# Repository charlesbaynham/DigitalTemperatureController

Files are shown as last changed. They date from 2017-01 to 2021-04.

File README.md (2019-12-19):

Digital Temperature Controller
==============================

_Copyright Charles Baynham 2018_

This repository holds a design for a digital temperature controller. The controller is designed for taking high precision
temperature measurements via a thermistor and applying low bandwidth PID feedback in response. 

This README file gives a brief overview of the device, but a much more detailed description is available in the manual, located in 
`./Manual`. 

`./Board design` contains schematics and PCB layouts for the controller board. This was produced in the open-source software KiCad. 

`./Code_for_microcontroller` contains the C++ code that must run on the on-board microcontroller. 

`./Code for Labview` contains a sample LabView application for controlling the device. See warning below...

Output
------

Output is by OPA458 high power opamps. Output can be up to 1A continuous, at voltages up to ±15V depending on the power supply.

Input
-----

Error signal acquisition is done by taking a balanced measurement between a thermistor
and a set resistor. The board produces an excitation voltage and measures
the difference in current between the thermistor and resistor to produce a temperature
measurement. For less demanding applications the set resistor can be on-board. For the
highest stability, the precision resistor should be placed next to its paired thermistor.
This measurement is performed by an INA330 chip, of which there are two present on
the board. The entire analogue section is electrically isolated from the rest of the board to
prevent noise on the electrical ground affecting the measurement.

Control
-------

The board can be controlled using a (virtual) serial connection over either USB or RS-485. Both of these interfaces 
are galvanically isolated to prevent electrical interference. The on-board microcontroller permits headless operation of the
device, and commands may be issued using a LabView interface.

Code
----

The code running on the device is written in c++ and has been well tested. The LabView control interface, designed to be run on a monitoring computer, is less well-tested and should be used at your own peril! For integration into an experimental system, control the device by issuing serial commands detail in the supplied manual. 

Manual
------

You should go read it now. It's in `./Manual`. 

Extensions
----------

The board is designed to break out the important analog (and come digital) connections, so that additional functionality can be enabled by adding a daughter-board to the main board. For example, you might 
* Require higher output currents
* Not need current driving capability, but would prefer very low-noise output instead
* Need an extreme level of stability, so use an external, ovenized voltage reference

None of these daughter-boards yet exist, but the interface required to create them exists from V5 onwards. 

Initial setup
-------------

The microcontroller needs to be flashed using Atmel Studio and an ISP programmer. You should either:

1. Set the fuses as described in `fuse_settings.txt`
2. Flash the bootloader saved as `optiboot_atmega328_custom_NANO.hex`
3. Use the Arduino IDE to compile and upload the latest version of the code

OR

1. Flash the complete production `.elf` file stored in `.\Code_for_microcontroller` using Atmel Studio, making sure to select "Flash", "Fuses" and "Verify Device ID" in Atmel Studio. This will give you whatever version of the code was stored in this `.elf` file, you can then update it using the Arduino IDE if you want to make changes.

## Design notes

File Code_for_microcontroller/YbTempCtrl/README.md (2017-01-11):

Yb+ temperature controller
==========================

Introduction  							{#sec-intro}
============

This is the source code for the Yb+ temperature controller, programmed and designed by <a href="mailto:charles.baynham@npl.co.uk">Charles Baynham</a>.

It is intended for high precision control of cavities, however can be used to control laser diode temperature or other low-bandwidth lock processes that could benefit from digital control. Error signal input can be either by voltage (from -5V to +5V) or through a balanced thermistor reading, mediated by a built-in INA330 IC. For demanding temperature applications, the latter method is recommended.

This code is designed to be uploaded to an ATMega328 microprocessor. It is written in C++ and can be compiled and uploaded via the Arduino IDE. However, if you intend to work on it for any significant length of time, I _highly_ recommend that you install a more capable IDE. I wrote this software in Visual Studio Community which is a free download from Microsoft and will make your life so much easier. 

Documentation 							{#sec-docs}
=============

If you are reading these comments in a pdf or html format then you are currently looking at the compiled documentation. If, however, you are reading this README.md file in a text editor then your first step before editing the code should be to get hold of the full code documentation. 

The code is documented throughout using the Doxygen commenting system. These can be compiled easily into a pdf or a local html website by:

1. Installing Doxygen from http://www.stack.nl/~dimitri/doxygen/download.html
2. Using the Doxygen GUI to load the file in this folder, `Doxyfile`
3. Selecting `Run doxygen` on the `Run` tab. 

This will produce the html documentation and, if you have pdflatex installed, source files for a pdf. 

Alternativly, open the Documentation.pdf file that should be bundled with this repo.  

Version Control 						{#sec-vc}
===============

This folder is a GIT repository that maintains a full history of development including every change since this code was started. This history is contained in a hidden folder called `.git` which should not be accessed directly. 

The upshot of this is that the code you see may not be the latest, and may instead be a "snapshot" of a previous state. To ensure you are looking at the latest iteration, and to make updates, install a git client of your choosing. https://windows.github.com/ is very lightweight, http://www.sourcetreeapp.com/ is more fully featured and https://desktop.github.com/ strikes a balance between the two.  

Once installed, "checkout" the master branch for the latest code version. See http://rogerdudler.github.io/git-guide/ for a simple guide. 

Note that this code makes use of several submodules. If you "clone" the code, you will by default not get these. In order to correctly get the code for these as well, run the command `git submodule update --init --recursive` after cloning the main code. If you use a more advanced GUI such as SourceTree then this should be handled for you automatically. 

Available commands						{#sec-commands}
=============

The device listens for commands on a virtual serial COM port served via USB. The USB connection is electrically isolated to avoid ground pollution. 

__Baud rate should be set to 57600.__

The board also contains footprints to enable RS485 communication via a backplane connection, however this is not yet implemented. 

For a detailed description of all the commands available, see the documentation for CommandDefinitions.h.

Code outline							{#sec-codeoutline}
=============

This code is split into classes according to the object orientated paradigm. A typical lock could be implemented as follows:

1. Define a YbCtrl::ErrorChannel object (or rather, an implementation of YbCtrl::ErrorChannel) to handle input.
2. Define a YbCtrl::CtrlChannel object to handle output
3. Define a YbCtrl::Algorithm object to implement the locking transfer function required.
4. Pass these three objects to a new YbCtrl::Controller object.
5. Loop, calling YbCtrl::Controller::doLoop() on each iteration. 

For more detail, every class and method is individually documented. See the Classes section or the Namespaces section to see more. 

@todo Implement RS485 Modbus protocol

@copyright Charles Baynham 2016

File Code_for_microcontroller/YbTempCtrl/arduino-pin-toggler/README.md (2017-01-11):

arduino-pin-toggler
===================

Introduction						{#sec-Introduction}
=============

This Arduino library manages the toggling of arbitary pins at controllable rates.
For example, it can be used to flash an LED at different speeds according
to the state of your device.

It works using interrupts and is designed to be lightweight when running,
so will not interfere with existing code.

This library requires exclusive usage of TIMER1 so is incompatible with
libraries that also use this timer.

Usage						{#sec-Usage}
=============

Include the class by adding `#include <pinToggler.h>` to your sketch.

Init the class by passing it an array of pins that will be toggled. E.g.

	int pins[3] = {13, A4, A5};
	pinToggler<3>::init(pins);

The template parameter (`<3>` above) defines the total number of pins being controlled.

These pins will start `LOW`, not toggling.

To start the toggling, set their speed to `OFF`, `SLOW`, `MEDIUM`, `FAST` or `MAX`. E.g.

	pinToggler<3>::setFlashRate(0, SLOW);

N.B. The template parameter (here `<3>`) must match the one used in pinToggler::init() or this will
throw an error. Also the LED parameter in pinToggler::setFlashRate refers to the pins passed to pinToggler::init(), zero-indexed
in the order that they appeared in in the array.

The speeds refer to fractions of the max speed, defined by #FLASH_FREQ_HZ.

@warning Note that all the function calls here are static members of the
class. Although a class object is created, this happens internally. For memory
management purposes, be aware that this class allocates `3 * numPins` bytes on
the heap. Thus, to avoid memory framentation, pinToggler::init() should be
called as early in your code as possible.

@copyright Charles Baynham 2016

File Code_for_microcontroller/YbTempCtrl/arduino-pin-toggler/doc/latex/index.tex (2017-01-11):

\hypertarget{index_Introduction}{}\section{Introduction}\label{index_Introduction}
This Arduino library manages the toggling of arbitary pins at controllable rates. For example, it can be used to flash an L\+ED at different speeds according to the state of your device.

It works using interrupts and is designed to be lightweight when running, so will not interfere with existing code.

This library requires exclusive usage of T\+I\+M\+E\+R1 so is incompatible with libraries that also use this timer.\hypertarget{index_Usage}{}\section{Usage}\label{index_Usage}
Include the class by adding {\ttfamily \#include $<$\hyperlink{pin_toggler_8h}{pin\+Toggler.\+h}$>$} to your sketch.

Init the class by passing it an array of pins that will be toggled. E.\+g. \begin{DoxyVerb}int pins[3] = {13, A4, A5};
pinToggler<3>::init(pins);
\end{DoxyVerb}

The template parameter ({\ttfamily $<$3$>$} above) defines the total number of pins being controlled.

These pins will start {\ttfamily L\+OW}, not toggling.

To start the toggling, set their speed to {\ttfamily O\+FF}, {\ttfamily S\+L\+OW}, {\ttfamily M\+E\+D\+I\+UM}, {\ttfamily F\+A\+ST} or {\ttfamily M\+AX}. E.\+g. \begin{DoxyVerb}pinToggler<3>::setFlashRate(0, SLOW);
\end{DoxyVerb}

N.\+B. The template parameter (here {\ttfamily $<$3$>$}) must match the one used in \hyperlink{classpin_toggler_aa58211817601d0e2dd413eb63e41f773}{pin\+Toggler\+::init()} or this will throw an error. Also the L\+ED parameter in \hyperlink{classpin_toggler_a42ae0ac4f841dae592195f26bffb109e}{pin\+Toggler\+::set\+Flash\+Rate} refers to the pins passed to \hyperlink{classpin_toggler_aa58211817601d0e2dd413eb63e41f773}{pin\+Toggler\+::init()}, zero-\/indexed in the order that they appeared in in the array.

The speeds refer to fractions of the max speed, defined by \hyperlink{pin_toggler_8h_a1097b75ec2a0f9ad2e6d4f6c4500d224}{F\+L\+A\+S\+H\+\_\+\+F\+R\+E\+Q\+\_\+\+HZ}.

\begin{DoxyWarning}{Warning}
Note that all the function calls here are static members of the class. Although a class object is created, this happens internally. For memory management purposes, be aware that this class allocates {\ttfamily 3 $\ast$ num\+Pins} bytes on the heap. Thus, to avoid memory framentation, \hyperlink{classpin_toggler_aa58211817601d0e2dd413eb63e41f773}{pin\+Toggler\+::init()} should be called as early in your code as possible.
\end{DoxyWarning}
\begin{DoxyCopyright}{Copyright}
Charles Baynham 2016 
\end{DoxyCopyright}

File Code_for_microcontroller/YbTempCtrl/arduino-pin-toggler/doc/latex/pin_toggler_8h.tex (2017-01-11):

\hypertarget{pin_toggler_8h}{}\section{pin\+Toggler.\+h File Reference}
\label{pin_toggler_8h}\index{pin\+Toggler.\+h@{pin\+Toggler.\+h}}

Contains all the code for the arduino-\/pin-\/toggler library.  

\subsection*{Classes}
\begin{DoxyCompactItemize}
\item 
class \hyperlink{classpin_toggler}{pin\+Toggler$<$ num\+Pins $>$}
\begin{DoxyCompactList}\small\item\em Class for toggling pins. \end{DoxyCompactList}\end{DoxyCompactItemize}
\subsection*{Macros}
\begin{DoxyCompactItemize}
\item 
\#define \hyperlink{pin_toggler_8h_a0fac869d83ac1a584d6c45cf609f5fe7}{P\+R\+E\+S\+C\+A\+L\+ER}~1024
\begin{DoxyCompactList}\small\item\em The prescaler for T\+I\+M\+E\+R1. \end{DoxyCompactList}\item 
\#define \hyperlink{pin_toggler_8h_a1097b75ec2a0f9ad2e6d4f6c4500d224}{F\+L\+A\+S\+H\+\_\+\+F\+R\+E\+Q\+\_\+\+HZ}~8
\begin{DoxyCompactList}\small\item\em How often the I\+SR will trigger. \end{DoxyCompactList}\end{DoxyCompactItemize}
\subsection*{Enumerations}

\subsection{Detailed Description}
Contains all the code for the arduino-\/pin-\/toggler library. 

\subsection{Macro Definition Documentation}
\index{pin\+Toggler.\+h@{pin\+Toggler.\+h}!F\+L\+A\+S\+H\+\_\+\+F\+R\+E\+Q\+\_\+\+HZ@{F\+L\+A\+S\+H\+\_\+\+F\+R\+E\+Q\+\_\+\+HZ}}
\index{F\+L\+A\+S\+H\+\_\+\+F\+R\+E\+Q\+\_\+\+HZ@{F\+L\+A\+S\+H\+\_\+\+F\+R\+E\+Q\+\_\+\+HZ}!pin\+Toggler.\+h@{pin\+Toggler.\+h}}
\subsubsection[{\texorpdfstring{F\+L\+A\+S\+H\+\_\+\+F\+R\+E\+Q\+\_\+\+HZ}{FLASH_FREQ_HZ}}]{\setlength{\rightskip}{0pt plus 5cm}\#define F\+L\+A\+S\+H\+\_\+\+F\+R\+E\+Q\+\_\+\+HZ~8}\hypertarget{pin_toggler_8h_a1097b75ec2a0f9ad2e6d4f6c4500d224}{}\label{pin_toggler_8h_a1097b75ec2a0f9ad2e6d4f6c4500d224}

How often the I\+SR will trigger. 

This defines the max toggle rate. In combination with the \hyperlink{pin_toggler_8h_a8f10e927d4361fa9c8ecfc7a0b163943}{F\+L\+A\+S\+H\+R\+A\+TE} chosen with \hyperlink{classpin_toggler_a42ae0ac4f841dae592195f26bffb109e}{pin\+Toggler\+::set\+Flash\+Rate}, this determines the rate at which the pins will toggle. \index{pin\+Toggler.\+h@{pin\+Toggler.\+h}!P\+R\+E\+S\+C\+A\+L\+ER@{P\+R\+E\+S\+C\+A\+L\+ER}}
\index{P\+R\+E\+S\+C\+A\+L\+ER@{P\+R\+E\+S\+C\+A\+L\+ER}!pin\+Toggler.\+h@{pin\+Toggler.\+h}}
\subsubsection[{\texorpdfstring{P\+R\+E\+S\+C\+A\+L\+ER}{PRESCALER}}]{\setlength{\rightskip}{0pt plus 5cm}\#define P\+R\+E\+S\+C\+A\+L\+ER~1024}\hypertarget{pin_toggler_8h_a0fac869d83ac1a584d6c45cf609f5fe7}{}\label{pin_toggler_8h_a0fac869d83ac1a584d6c45cf609f5fe7}

The prescaler for T\+I\+M\+E\+R1. 

This value is used to calculate the correct value to start T\+I\+M\+E\+R1 on, given this prescaler factor.

This does not need to be changed unless you need particularly fast flash rates.

Specifically, if your application requires {\ttfamily 16000000 / P\+R\+E\+S\+C\+A\+L\+ER / F\+L\+A\+S\+H\+\_\+\+F\+R\+E\+Q\+\_\+\+HZ $>$= 65536} you will need to alter the prescaler value both here and where it is set in the private setup\+Singleton() method. 

\subsection{Enumeration Type Documentation}
\index{pin\+Toggler.\+h@{pin\+Toggler.\+h}!F\+L\+A\+S\+H\+R\+A\+TE@{F\+L\+A\+S\+H\+R\+A\+TE}}
\index{F\+L\+A\+S\+H\+R\+A\+TE@{F\+L\+A\+S\+H\+R\+A\+TE}!pin\+Toggler.\+h@{pin\+Toggler.\+h}}
\subsubsection[{\texorpdfstring{F\+L\+A\+S\+H\+R\+A\+TE}{FLASHRATE}}]{\setlength{\rightskip}{0pt plus 5cm}enum {\bf F\+L\+A\+S\+H\+R\+A\+TE}}\hypertarget{pin_toggler_8h_a8f10e927d4361fa9c8ecfc7a0b163943}{}\label{pin_toggler_8h_a8f10e927d4361fa9c8ecfc7a0b163943}

Flash rate options. 

These rates are used as parameters to the set\+Flash\+Rate method.

In combination with F\+L\+A\+S\+H\+\_\+\+F\+R\+E\+Q\+\_\+\+HZ, these set the flash rate of an L\+ED.

O\+FF and ON allow you to disable flashing, leaving the L\+ED either on or off. \begin{Desc}
\item[Enumerator]\par
\begin{description}
\index{ON@{ON}!pin\+Toggler.\+h@{pin\+Toggler.\+h}}\index{pin\+Toggler.\+h@{pin\+Toggler.\+h}!ON@{ON}}\item[{\em 
ON\hypertarget{pin_toggler_8h_a8f10e927d4361fa9c8ecfc7a0b163943a977d478dacaae531f95695750d1e9d03}{}\label{pin_toggler_8h_a8f10e927d4361fa9c8ecfc7a0b163943a977d478dacaae531f95695750d1e9d03}
}]Always on \index{O\+FF@{O\+FF}!pin\+Toggler.\+h@{pin\+Toggler.\+h}}\index{pin\+Toggler.\+h@{pin\+Toggler.\+h}!O\+FF@{O\+FF}}\item[{\em 
O\+FF\hypertarget{pin_toggler_8h_a8f10e927d4361fa9c8ecfc7a0b163943aac132f2982b98bcaa3445e535a03ff75}{}\label{pin_toggler_8h_a8f10e927d4361fa9c8ecfc7a0b163943aac132f2982b98bcaa3445e535a03ff75}
}]Always off \index{S\+L\+OW@{S\+L\+OW}!pin\+Toggler.\+h@{pin\+Toggler.\+h}}\index{pin\+Toggler.\+h@{pin\+Toggler.\+h}!S\+L\+OW@{S\+L\+OW}}\item[{\em 
S\+L\+OW\hypertarget{pin_toggler_8h_a8f10e927d4361fa9c8ecfc7a0b163943ab27edad9d3e126dc8448b6030438adb6}{}\label{pin_toggler_8h_a8f10e927d4361fa9c8ecfc7a0b163943ab27edad9d3e126dc8448b6030438adb6}
}]Flash at F\+L\+A\+S\+H\+\_\+\+F\+R\+E\+Q\+\_\+\+HZ / 8 \index{M\+E\+D\+I\+UM@{M\+E\+D\+I\+UM}!pin\+Toggler.\+h@{pin\+Toggler.\+h}}\index{pin\+Toggler.\+h@{pin\+Toggler.\+h}!M\+E\+D\+I\+UM@{M\+E\+D\+I\+UM}}\item[{\em 
M\+E\+D\+I\+UM\hypertarget{pin_toggler_8h_a8f10e927d4361fa9c8ecfc7a0b163943a5340ec7ecef6cc3886684a3bd3450d64}{}\label{pin_toggler_8h_a8f10e927d4361fa9c8ecfc7a0b163943a5340ec7ecef6cc3886684a3bd3450d64}
}]Flash at F\+L\+A\+S\+H\+\_\+\+F\+R\+E\+Q\+\_\+\+HZ / 2 \index{F\+A\+ST@{F\+A\+ST}!pin\+Toggler.\+h@{pin\+Toggler.\+h}}\index{pin\+Toggler.\+h@{pin\+Toggler.\+h}!F\+A\+ST@{F\+A\+ST}}\item[{\em 
F\+A\+ST\hypertarget{pin_toggler_8h_a8f10e927d4361fa9c8ecfc7a0b163943af84c11ba888e499a8a282a3e6f5de7de}{}\label{pin_toggler_8h_a8f10e927d4361fa9c8ecfc7a0b163943af84c11ba888e499a8a282a3e6f5de7de}
}]Flash at F\+L\+A\+S\+H\+\_\+\+F\+R\+E\+Q\+\_\+\+HZ / 4 \index{M\+AX@{M\+AX}!pin\+Toggler.\+h@{pin\+Toggler.\+h}}\index{pin\+Toggler.\+h@{pin\+Toggler.\+h}!M\+AX@{M\+AX}}\item[{\em 
M\+AX\hypertarget{pin_toggler_8h_a8f10e927d4361fa9c8ecfc7a0b163943ad7e097bda6d981de2520f49fe74c25b7}{}\label{pin_toggler_8h_a8f10e927d4361fa9c8ecfc7a0b163943ad7e097bda6d981de2520f49fe74c25b7}
}]Flash at F\+L\+A\+S\+H\+\_\+\+F\+R\+E\+Q\+\_\+\+HZ \end{description}
\end{Desc}

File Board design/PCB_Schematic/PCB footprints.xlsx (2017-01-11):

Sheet: 1.25mm pitch, two rows
1 | $PAD^^nSh "1" R 1.5 1.5 0 0 0^^nDr 0.8 0 0^^nAt STD N 00E0FFFF^^nNe 1 ""^^nPo 0 0^^n$EndPAD | 2 | $PAD^^nSh "2" C 1.5 1.5 0 0 0^^nDr 0.8 0 0^^nAt STD N 00E0FFFF^^nNe 1 ""^^nPo 1.25 -5^^n$EndPAD
3 | $PAD^^nSh "3" C 1.5 1.5 0 0 0^^nDr 0.8 0 0^^nAt STD N 00E0FFFF^^nNe 1 ""^^nPo 2.5 0^^n$EndPAD | 4 | $PAD^^nSh "4" C 1.5 1.5 0 0 0^^nDr 0.8 0 0^^nAt STD N 00E0FFFF^^nNe 1 ""^^nPo 3.75 -5^^n$EndPAD
5 | $PAD^^nSh "5" C 1.5 1.5 0 0 0^^nDr 0.8 0 0^^nAt STD N 00E0FFFF^^nNe 1 ""^^nPo 5 0^^n$EndPAD | 6 | $PAD^^nSh "6" C 1.5 1.5 0 0 0^^nDr 0.8 0 0^^nAt STD N 00E0FFFF^^nNe 1 ""^^nPo 6.25 -5^^n$EndPAD
7 | $PAD^^nSh "7" C 1.5 1.5 0 0 0^^nDr 0.8 0 0^^nAt STD N 00E0FFFF^^nNe 1 ""^^nPo 7.5 0^^n$EndPAD | 8 | $PAD^^nSh "8" C 1.5 1.5 0 0 0^^nDr 0.8 0 0^^nAt STD N 00E0FFFF^^nNe 1 ""^^nPo 8.75 -5^^n$EndPAD
9 | $PAD^^nSh "9" C 1.5 1.5 0 0 0^^nDr 0.8 0 0^^nAt STD N 00E0FFFF^^nNe 1 ""^^nPo 10 0^^n$EndPAD | 10 | $PAD^^nSh "10" C 1.5 1.5 0 0 0^^nDr 0.8 0 0^^nAt STD N 00E0FFFF^^nNe 1 ""^^nPo 11.25 -5^^n$EndPAD
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

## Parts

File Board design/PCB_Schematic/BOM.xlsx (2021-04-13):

Ref | Value | Part | Footprint | Description | MPN | SPURL | MFR | SPR | SPN
C_filter1,C_filter2 | 1n | Device:C | Capacitor_SMD:C_0805_2012Metric_Pad1.15x1.40mm_HandSolder | Unpolarized capacitor | - | - | - | - | GENERIC
C1 | 22u | Device:C | Capacitors_ThroughHole:C_Radial_D5_L11_P2 | Unpolarized capacitor | - | - | - | - | GENERIC
C12,C13,C20,C21,C26,C27,C37,C38,C43,C45,C46,C47,C50,C52,C53,C54 | 100n | Device:CP | Capacitor_SMD:C_0805_2012Metric_Pad1.15x1.40mm_HandSolder | Polarized capacitor | - | - | - | - | GENERIC
C14,C15,C22,C23 | 100p | Device:C_Small | Capacitor_SMD:C_0805_2012Metric_Pad1.15x1.40mm_HandSolder | Unpolarized capacitor, small symbol | - | - | - | - | GENERIC
C2,C5 | 47u | Device:CP | Capacitors_ThroughHole:C_Radial_D5_L11_P2 | Polarized capacitor | - | - | - | - | GENERIC
C28 | 1u | Device:CP_Small | Capacitor_SMD:C_0805_2012Metric_Pad1.15x1.40mm_HandSolder | Polarized capacitor, small symbol | - | - | - | - | GENERIC
C29,C31,C34 | 100n | Device:CP_Small | Capacitor_SMD:C_0805_2012Metric_Pad1.15x1.40mm_HandSolder | Polarized capacitor, small symbol | - | - | - | - | GENERIC
C3,C4,C10,C11,C18,C19,C35,C36,C48,C55 | 1u | Device:CP | Capacitor_SMD:C_0805_2012Metric_Pad1.15x1.40mm_HandSolder | Polarized capacitor | - | - | - | - | GENERIC
C30,C32 | 8p | Device:C_Small | Capacitor_SMD:C_0805_2012Metric_Pad1.15x1.40mm_HandSolder | Unpolarized capacitor, small symbol | - | - | - | - | GENERIC
C33 | 100n | Device:C | Capacitor_SMD:C_0805_2012Metric_Pad1.15x1.40mm_HandSolder | Unpolarized capacitor | - | - | - | - | GENERIC
C39 | 4.7n | Device:C | Capacitor_SMD:C_0805_2012Metric_Pad1.15x1.40mm_HandSolder | Unpolarized capacitor | - | - | - | - | GENERIC
C40,C41 | 1u | Device:C | Capacitor_SMD:C_0805_2012Metric_Pad1.15x1.40mm_HandSolder | Unpolarized capacitor | - | - | - | - | GENERIC
C42,C44,C49,C51 | 15p | Device:C | Capacitor_SMD:C_0805_2012Metric_Pad1.15x1.40mm_HandSolder | Unpolarized capacitor | - | - | - | - | GENERIC
C57,C58 | 100n | Device:C_Small | Capacitor_SMD:C_0805_2012Metric_Pad1.15x1.40mm_HandSolder | Unpolarized capacitor, small symbol | - | - | - | - | GENERIC
C6,C7,C56 | 1u | Device:C_Small | Capacitor_SMD:C_0805_2012Metric_Pad1.15x1.40mm_HandSolder | Unpolarized capacitor, small symbol | - | - | - | - | GENERIC
C8,C9 | 10n | Device:C | Capacitor_SMD:C_0805_2012Metric_Pad1.15x1.40mm_HandSolder | Unpolarized capacitor | - | - | - | - | GENERIC
CON1 | BARREL_JACK | Connector:Barrel_Jack_Switch | Connector_BarrelJack:BarrelJack_Horizontal | DC Barrel Jack with an internal switch | 448-382 | - | RS Pro | RS | 448-382
D1 | Led_x2_split | Custom_Components:Led_x2_split | Custom:Double_LEDs |  | L-710A8MD/2ID | - | Kingbright | RS | 6164188
D2 | POWER | Device:LED | LEDs:LED_0805 | Light emitting diode | LG R971 | - | OSRAM | RS | 654-5773
D3 | TX | Device:LED | LEDs:LED_0805 | Light emitting diode | LG R971 | - | OSRAM | RS | 654-5773
D4 | RX | Device:LED | LEDs:LED_0805 | Light emitting diode | LG R971 | - | OSRAM | RS | 654-5773
D5 | SCLK | Device:LED | LEDs:LED_0805 | Light emitting diode | LG R971 | - | OSRAM | RS | 654-5773
D6 | LED | Device:LED | Custom:PCB_MOUNT_LED | Light emitting diode | L-93A8CB/1GD | - | Kingbright | RS | 466-4260
DB_ES1,DB_ES2,DB_OPA1,DB_OPA2 | PIN | Connector:Conn_01x01_Female | TestPoint:TestPoint_THTPad_1.5x1.5mm_Drill0.7mm | Generic connector, single row, 01x01, script generated (kicad-library-utils/schlib/autogen/connector/) | DNP | DNP | DNP | DNP | DNP
DB_GND1,DB_GND2,DB_GND3,DB_5V1,DB_VCC1,DB_VCC2,DB_VCC3 | PIN | Connector:Conn_01x01_Female | TestPoint:TestPoint_THTPad_3.0x3.0mm_Drill1.5mm | Generic connector, single row, 01x01, script generated (kicad-library-utils/schlib/autogen/connector/) | DNP | DNP | DNP | DNP | DNP
DISABLE_OPA1 | Disable_OPA1 | Jumper:Jumper_3_Bridged12 | Jumper:SolderJumper-3_P1.3mm_Bridged2Bar12_Pad1.0x1.5mm_NumberLabels | Jumper, 3-pole, pins 1+2 closed/bridged | DNP | DNP | DNP | DNP | DNP
DISABLE_OPA2 | Disable_OPA2 | Jumper:Jumper_3_Bridged12 | Jumper:SolderJumper-3_P1.3mm_Bridged2Bar12_Pad1.0x1.5mm_NumberLabels | Jumper, 3-pole, pins 1+2 closed/bridged | DNP | DNP | DNP | DNP | DNP
DISABLE_OPA3 | Disable_OPA3 | Jumper:Jumper_3_Bridged12 | Jumper:SolderJumper-3_P1.3mm_Bridged2Bar12_Pad1.0x1.5mm_NumberLabels | Jumper, 3-pole, pins 1+2 closed/bridged | DNP | DNP | DNP | DNP | DNP
DISABLE_OPA4 | Disable_OPA4 | Jumper:Jumper_3_Bridged12 | Jumper:SolderJumper-3_P1.3mm_Bridged2Bar12_Pad1.0x1.5mm_NumberLabels | Jumper, 3-pole, pins 1+2 closed/bridged | DNP | DNP | DNP | DNP | DNP
IC1 | ATMEGA328P-A | MCU_Microchip_ATmega:ATmega328P-AU | Housings_QFP:LQFP-32_7x7mm_Pitch0.8mm | 20MHz, 32kB Flash, 2kB SRAM, 1kB EEPROM, TQFP-32 | ATMEGA328P-A | - | Atmel | Farnell | 1715486
J1 | 5V_Outputs_1 | Connector_Generic:Conn_01x03 | Connector_PinHeader_2.54mm:PinHeader_1x03_P2.54mm_Vertical | Generic connector, single row, 01x03, script generated (kicad-library-utils/schlib/autogen/connector/) | - | - | - | - | GENERIC
J2 | External 2.5v ref | Connector:Conn_Coaxial | Connector_Coaxial:MMCX_Molex_73415-1471_Vertical | coaxial connector (BNC, SMA, SMB, SMC, Cinch/RCA, ...) | 73415-1471 | - | Molex | Digi-Key | WM5557-ND
J3 | 5V_Outputs_2 | Connector_Generic:Conn_01x03 | Connector_PinHeader_2.54mm:PinHeader_1x03_P2.54mm_Vertical | Generic connector, single row, 01x03, script generated (kicad-library-utils/schlib/autogen/connector/) | - | - | - | - | GENERIC
JP1 | DISABLE FLASH | Device:Jumper_NC_Dual | Pin_Headers:Pin_Header_Straight_1x03 | Dual jumper, normally closed | 09.03290.01 | - | EOZ | RS | 204-7865
JP2,JP3,JP4,JP5,JP6,JP7 | Jumper_NO_Small | Device:Jumper_NO_Small | Custom:SmallJumperNoCourtyard | Jumper, normally open, small symbol | DNP | DNP | DNP | DNP | DNP
P1 | 233-2977 | Connector_Generic:Conn_02x04_Odd_Even | Custom:Molex_Microfit3_Header_02x04_Angled_43045-080x_FIXED | Generic connector, double row, 02x04, odd/even pin numbering scheme (row 1 odd numbers, row 2 even numbers), script generated (kicad-library-utils/schlib/autogen/connector/) | 43045-0800 | - | Molex | RS | 233-2977
P2 | 820-8104 | Connector_Generic:Conn_01x08 | Custom:RJ45_TE | Generic connector, single row, 01x08, script generated (kicad-library-utils/schlib/autogen/connector/) | 1-406525-1 | - | TE Connectivity | RS | 820-8104
P3 | RS485 | Connector_Generic:Conn_01x04 | Connectors_Molex:Molex_PicoBlade_53048-0410_04x1.25mm_Angled | Generic connector, single row, 01x04, script generated (kicad-library-utils/schlib/autogen/connector/) | 53048-0410 | - | Molex | Digikey | WM1744-ND
P4 | USB_OTG | Connector:USB_OTG | Custom:MICRO-B_USB_TOP_MOUNT | USB mini/micro connector | 47590-0001 | - | MOLEX | Farnell | 1568022
P5 | ICSP | Connector_Generic:Conn_02x03_Odd_Even | Pin_Headers:Pin_Header_Straight_2x03 | Generic connector, double row, 02x03, odd/even pin numbering scheme (row 1 odd numbers, row 2 even numbers), script generated (kicad-library-utils/schlib/autogen/connector/) | 75869-131LF | - | Amphenol FCI | Digikey | 609-2845-ND
P6 | ADC breakout | Connector_Generic:Conn_02x04_Odd_Even | Pin_Headers:Pin_Header_Straight_2x04_Pitch1.27mm | Generic connector, double row, 02x04, odd/even pin numbering scheme (row 1 odd numbers, row 2 even numbers), script generated (kicad-library-utils/schlib/autogen/connector/) | DNP | DNP | DNP | DNP | DNP
R_gain1,R_gain2 | 22k_prec | Device:R | Resistor_SMD:R_0805_2012Metric_Pad1.15x1.40mm_HandSolder | Resistor | RG2012L-223-L-T05 | - | Susumu | Digikey | 408-1781-1-ND
R_Prec1,R_Prec2 | 10k_prec | Device:R | Custom:Resistor_Vertical_RM5mm_Cust | Resistor | Y0706-10KA-ND | - | Vishay | Digikey | Y0706-10KA-ND
R_Prec3 | 33k_prec | Device:R_Small | Resistor_SMD:R_0805_2012Metric_Pad1.15x1.40mm_HandSolder | Resistor, small symbol | RG2012L-333-L-T05 | - | Susumu | Digikey | 408-1781-1-ND
R_Prec4 | 22k_prec | Device:R_Small | Resistor_SMD:R_0805_2012Metric_Pad1.15x1.40mm_HandSolder | Resistor, small symbol | RG2012L-223-L-T05 | - | Susumu | Digikey | 408-1781-1-ND
R_R1,R_R2,R_T1,R_T2 | 1k_prec | Device:R_Small | Resistor_SMD:R_0805_2012Metric_Pad1.15x1.40mm_HandSolder | Resistor, small symbol | RG2012L-102-L-T05 | - | Susumu | Digikey | 408-1774-1-ND
R1,R2,R26,R29,R30,R31,R34,R37,R38,R39,R43 | 100R | Device:R | Resistor_SMD:R_0805_2012Metric_Pad1.15x1.40mm_HandSolder | Resistor | - | - | - | - | GENERIC
R10 | 1k | Device:R | Resistor_SMD:R_0805_2012Metric_Pad1.15x1.40mm_HandSolder | Resistor | - | - | - | - | GENERIC
R11,R40,R41,R42 | 10k | Device:R_Small | Resistor_SMD:R_0805_2012Metric_Pad1.15x1.40mm_HandSolder | Resistor, small symbol | - | - | - | - | GENERIC
R12,R14,R16,R18 | 51K | Device:R | Resistor_SMD:R_0805_2012Metric_Pad1.15x1.40mm_HandSolder | Resistor | - | - | - | - | GENERIC
R13,R15,R17,R19 | 200K | Device:R | Resistor_SMD:R_0805_2012Metric_Pad1.15x1.40mm_HandSolder | Resistor | - | - | - | - | GENERIC
R20,R_Ser1,R_Ser2 | 1k | Device:R_Small | Resistor_SMD:R_0805_2012Metric_Pad1.15x1.40mm_HandSolder | Resistor, small symbol | - | - | - | - | GENERIC
R3,R4,R5,R21,R22,R23 | 100R | Device:R_Small | Resistor_SMD:R_0805_2012Metric_Pad1.15x1.40mm_HandSolder | Resistor, small symbol | - | - | - | - | GENERIC
R8 | RS485_TERM | Device:R_Small | Resistor_THT:R_Axial_DIN0516_L15.5mm_D5.0mm_P5.08mm_Vertical | Resistor, small symbol | DNP | DNP | DNP | DNP | DNP
R9,R24,R25,R27,R28,R32,R33,R35,R36 | 10k | Device:R | Resistor_SMD:R_0805_2012Metric_Pad1.15x1.40mm_HandSolder | Resistor | - | - | - | - | GENERIC
SELECT_VRef1 | Select V_ref | Jumper:Jumper_3_Bridged12 | Jumper:SolderJumper-3_P1.3mm_Bridged2Bar12_Pad1.0x1.5mm_NumberLabels | Jumper, 3-pole, pins 1+2 closed/bridged | DNP | DNP | DNP | DNP | DNP
SW1 | DISABLE_COMMS | Switch:SW_SPDT | Custom:ApemSwitch | Switch, single pole double throw | TL36WW050 | - | APEM | RS | 664-288
U1 | LM7805 | Custom_Components:7805_mod | Custom:TO220_HORZ |  | LM7805CT/NOPB | - | Texas Instruments | Digikey | 296-47192-ND
U11 | ISO7242 | Custom_Components:ISO7242 | Housings_SOIC:SOIC-16_7.5x10.3mm_Pitch1.27mm |  | ISO7242 | - | TI | Mouser | 595-ISO7242CDW
U12 | FT232RL | Custom_Components:FT232RL | Housings_SSOP:SSOP-28_5.3x10.2mm_Pitch0.65mm |  | FT232RL | - | FTDI | Farnell | 1146032
U13 | ADS1262 | Custom_Components:ADS1262 | Housings_SSOP:TSSOP-28_4.4x9.7mm_Pitch0.65mm |  | ADS1262IPW | - | Texas Instruments | Farnell | 2494428
U14,U16 | AD8639 | Custom_Components:AD8639 | Housings_SOIC:SOIC-8_3.9x4.9mm_Pitch1.27mm |  | AD8639ARZ | - | Analog Devices | Farnell | 2067779
U15,U17 | DAC8564 | Custom_Components:DAC8564 | Housings_SSOP:TSSOP-16_4.4x5mm_Pitch0.65mm |  | DAC8564IDPW | - | Texas Instruments | Farnell | 2496193
U18 | 74LS125 | 74xx:74LS125 | Package_SO:TSSOP-14_4.4x5mm_P0.65mm | Quad buffer 3-State outputs | SN74LS125ADBR | - | Texas Instruments | Digikey | 296-31847-2-ND
U2 | TMA0505S | Custom_Components:TMA0505S | Custom:SIP_TMA0505 |  | TMA0505S | - | Traco Power | Digikey | 1951-1003-ND
U3 | ADuM7642CRQZ | Custom_Components:ADuM7642 | Housings_SSOP:SSOP-20_4.4x6.5mm_Pitch0.65mm | ADuM7642 6 channel digital isolator | ADUM7642CRQZ | - | Analog Devices | Farnell | 2254976
U4 | ISO3088 | Custom_Components:ISO3088 | Housings_SOIC:SOIC-16W_7.5x10.3mm_Pitch1.27mm | Full isolated 10MBps Fail-Safe RS-485/J1708 Transceiver | ISO3088DW | - | Texas Instruments | Farnell | 1755042
U5,U6,U7,U8 | OPA548 | Custom_Components:OPA548 | Custom:TO-263-7Lead |  | OPA548F/500 | - | Texas Instruments | Farnell | 2496316
U9,U10 | INA330 | Custom_Components:INA330 | Housings_SSOP:MSOP-10_3x3mm_Pitch0.5mm |  | INA330AIDGST | - | Texas Instruments | Farnell | 2496434
W1 | INA1 | Connector:TestPoint | TestPoint:TestPoint_Loop_D2.50mm_Drill1.0mm | test point | DNP | DNP | DNP | DNP | DNP
W10 | VLIM2 | Connector:TestPoint | TestPoint:TestPoint_Loop_D2.50mm_Drill1.0mm | test point | DNP | DNP | DNP | DNP | DNP
W2 | GND_ISO | Connector:TestPoint | TestPoint:TestPoint_Loop_D2.50mm_Drill1.0mm | test point | DNP | DNP | DNP | DNP | DNP
W3 | 2.5V | Connector:TestPoint | TestPoint:TestPoint_Loop_D2.50mm_Drill1.0mm | test point | DNP | DNP | DNP | DNP | DNP
W4 | 5V_ISO | Connector:TestPoint | TestPoint:TestPoint_Loop_D2.50mm_Drill1.0mm | test point | DNP | DNP | DNP | DNP | DNP
W5 | OPA1_IN+ | Connector:TestPoint | TestPoint:TestPoint_Loop_D2.50mm_Drill1.0mm | test point | DNP | DNP | DNP | DNP | DNP
W6 | OPA1_IN- | Connector:TestPoint | TestPoint:TestPoint_Loop_D2.50mm_Drill1.0mm | test point | DNP | DNP | DNP | DNP | DNP
W7 | VLIM1 | Connector:TestPoint | TestPoint:TestPoint_Loop_D2.50mm_Drill1.0mm | test point | DNP | DNP | DNP | DNP | DNP
W8 | OPA2_IN+ | Connector:TestPoint | TestPoint:TestPoint_Loop_D2.50mm_Drill1.0mm | test point | DNP | DNP | DNP | DNP | DNP
W9 | OPA2_IN- | Connector:TestPoint | TestPoint:TestPoint_Loop_D2.50mm_Drill1.0mm | test point | DNP | DNP | DNP | DNP | DNP
X1 | TSX-3225 X1E0000210013 | Device:Crystal_GND3 | Crystals:crystal_FA238-TSX3225 | Three pin crystal, GND on pin 3 | X1E0000210013 TSX-3225 16 MHZ 9.0PF | - | EPSON | Farnell | 1712841

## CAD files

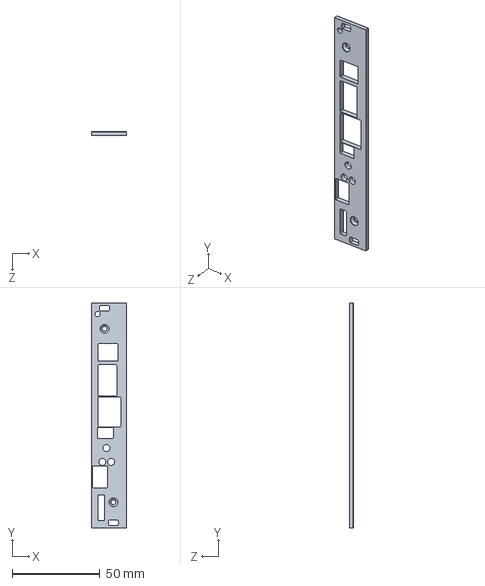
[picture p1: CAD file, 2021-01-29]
Board design/Rack mounting/Temperature controller V5 - 3U4HP.SLDPRT
20.0 x 128.4 x 2.50 mm

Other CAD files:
Board design/SolidworksRender.SLDPRT
Board design/Rack mounting/Temperature controller V5 - 3U4HP.SLDDRW

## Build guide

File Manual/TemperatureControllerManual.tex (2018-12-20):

\documentclass[11pt]{report}
\usepackage{geometry}                % See geometry.pdf to learn the layout options. There are lots.
\geometry{a4paper}                   % ... or a4paper or a5paper or ... 
%\geometry{landscape}                % Activate for for rotated page geometry
%\usepackage[parfill]{parskip}    % Activate to begin paragraphs with an empty line rather than an indent

% Custom doxygen styles, packaged as an envronment instead
\usepackage{mydoxygen}

\usepackage{pdfpages}
\usepackage{graphicx}
\usepackage{float}
\usepackage{amssymb}
\usepackage[disable]{todonotes}
\usepackage{epstopdf}
\usepackage{hyperref}
\usepackage{wrapfig}
\usepackage{siunitx}
\usepackage[version=3]{mhchem} % For chemical typesetting
\usepackage[toc,page]{appendix}
\usepackage{booktabs}
\DeclareGraphicsRule{.tif}{png}{.png}{`convert #1 `dirname #1`/`basename #1 .tif`.png}

% Make subtitle
\usepackage{titling}
\newcommand{\subtitle}[1]{%
  \posttitle{%
    \par\end{center}
    \begin{center}\textit{\large#1}\end{center}
    \vskip0.5em}%
}

\graphicspath{{images/}}

% Define numbers
\newcommand{\baudrate}{57600}
\newcommand{\VExcite}{1.0}
\newcommand{\RGain}{\SI{51}{\kilo\ohm}}
\newcommand{\RSeries}{\SI{1}{\kilo\ohm}}
\newcommand{\RSet}{\SI{10}{\kilo\ohm}}
\newcommand{\tempRange}{\SI{7}{\celsius} to \SI{36}{\celsius}}

\newcommand{\tempCtrlVer}{v4.3D}

\title{Digital isolated 4 channel temperature controller}
\subtitle{Version: \tempCtrlVer}
\author{Charles Baynham}
\date{\today}                                           % Activate to display a given date or no date

\setlength{\parskip}{4mm plus 4mm minus 2mm}

% Call chapters "sections"
\renewcommand{\chaptername}{Section}

\begin{document}
\maketitle

\tableofcontents
\clearpage

\chapter{Overview} % (fold)
\label{sec:overview}

\begin{figure}[h]
	\centering
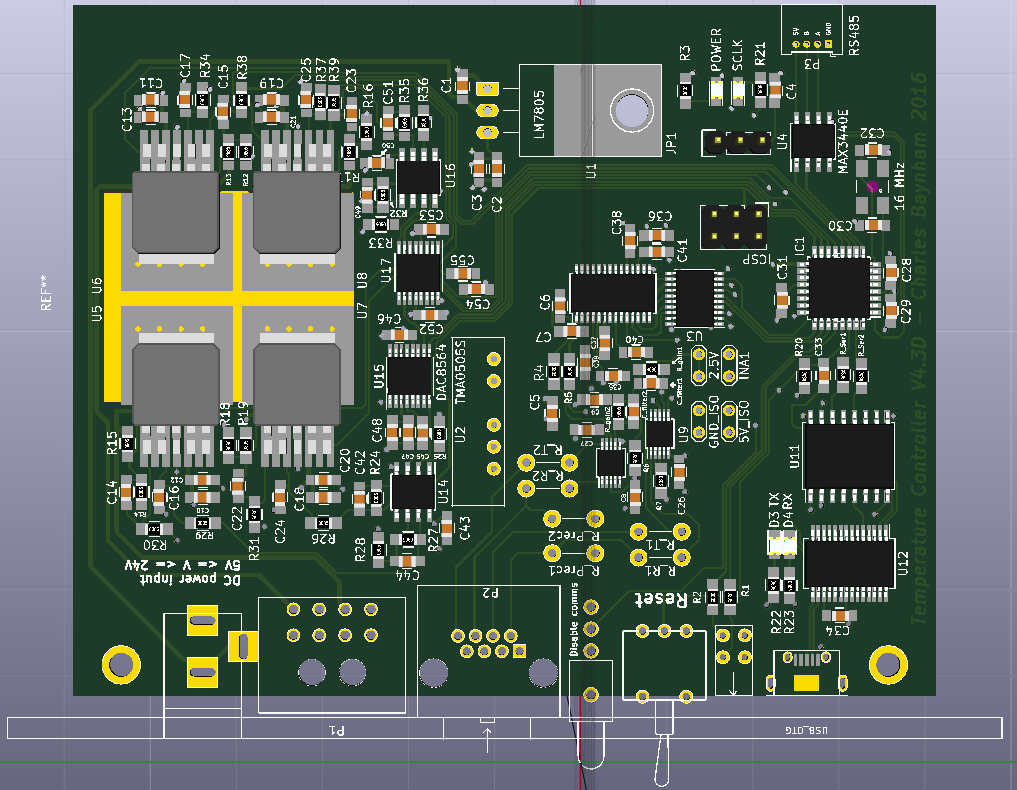
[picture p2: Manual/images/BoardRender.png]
	
	\caption{Picture / render of the board}
	\label{fig:wholeboard}
\end{figure}

This manual describes the operation and design processes behind the \ce{Yb+} digital temperature controller, version~\tempCtrlVer. The controller is designed for taking high precision temperature measurements via a thermistor and applying low bandwidth PID feedback in response.

\section{Microprocessor}

The device is controlled by an on-board microprocessor running at \SI{16}{MHz}. It operates in headless mode and can be configured to automatically recover from power failures. Setup and monitoring is by USB connection, baud rate 57600. This USB connection is electrically isolated from the rest of the board to prevent ground loops or digital noise. 

\section{Output}

Output is by either OPA458 high power opamps. Output can be up to \SI{1}{\A} continuous (see Figure~\ref{fig:OPA_SOA}), at voltages up to \SI{24}{\volt} depending on the power supply, $V_S$. 

The board contains space for four output channels allowing for voltages between \SI{0}{\volt} and $V_S$. Alternatively the channels can be combined to form two bipolar output channels, permitting outputs up to $\pm V_S$. See Section~\ref{sec:connector_pins} for details. Note that these are not rail-to-rail opamps: the minimum possible output is around \SI{300}{\milli\volt}, so applications that require lower voltages than these must use the bipolar configuration. 

\section{Input}

Error signal acquisition is done by taking a balanced measurement between a thermistor and a set resistor. The board produces an excitation voltage, usually \SI{\VExcite}{\volt}, and measures the difference in current between the thermistor and resistor to produce a temperature measurement. For less demanding applications the set resistor can be on-board. For the highest stability, the precision resistor should be placed next to its paired thermistor. 

This measurement is performed by an INA330 chip, of which there are two present on the board. The entire analogue section is electrically isolated from the rest of the board to prevent noise on the electrical ground affecting the measurement. 

There are therefore two possible input channels by balanced thermistor measurements. See Section~\ref{sec:connector_pins} for details. 

\section{Commands}

Control of the device is via serial connection over USB. It accepts commands, detailed in Appendix~\ref{chap:available_commands}. A Labview interface is also available which handles this communication. 

\chapter{Connector Pins} % (fold)
\label{sec:connector_pins}

This section describes the usage and pin-out for all the connectors on the board. See Figure~\ref{fig:connectors} for reference as to their locations. 

\begin{figure}[h!]
	\centering
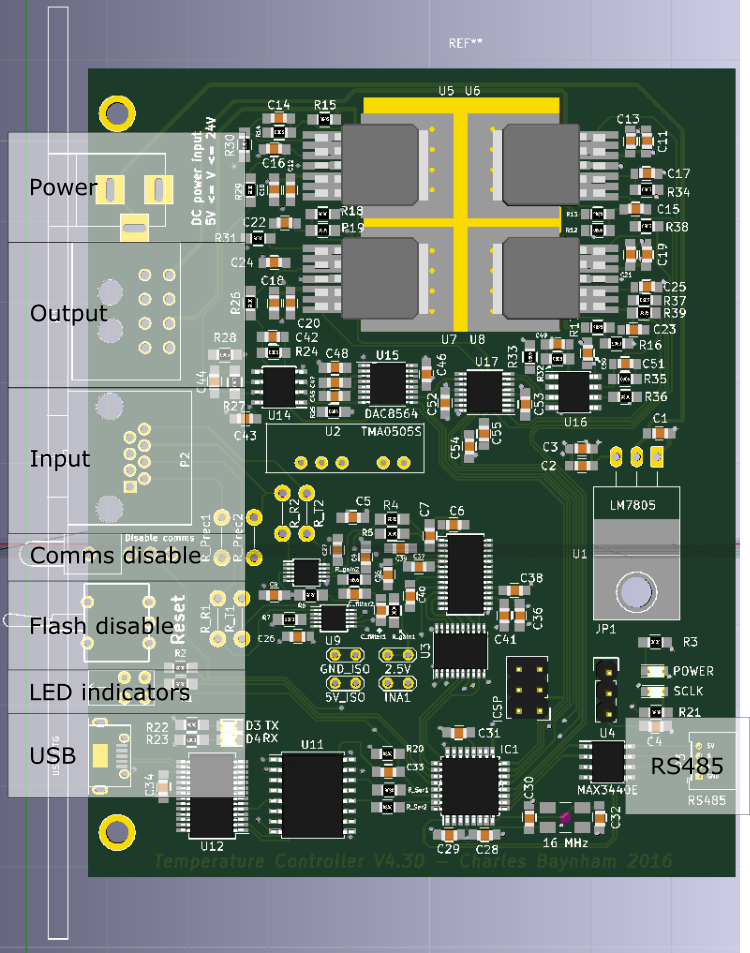
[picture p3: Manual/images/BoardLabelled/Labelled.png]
	
	\caption{Layout of connectors on the board}
	\label{fig:connectors}
\end{figure}

\section{Power}

Power supply is via a standard \SI{2.1}{mm}, centre-positive barrel connector. The board expects a DC voltage up to \SI{30}{\volt} and of at least \SI{7}{\volt}, limited by the LM7805 power regulator that powers most of the electronics. Whatever voltage is supplied here will be the maximum possible output control voltage. When choosing what voltage to supply, the user should take note of considerations in Section~\ref{sub:opa_choice} regarding opamp overheating. 

\section{Output}

\begin{table}[H]
	
	\centering

	\begin{tabular}{ll}
	\toprule
	Pin & Purpose  \\ \midrule
	1   & GND      \\
	2   & GND      \\
	3   & GND      \\
	4   & GND      \\
	5   & Unipolar output 1 or bipolar 1 positive output ({\tt BPA}) \\
	6   & Unipolar output 2 or bipolar 1 negative output ({\tt BPA}) \\
	7   & Unipolar output 3 or bipolar 2 positive output ({\tt BPB}) \\
	8   & Unipolar output 4 or bipolar 2 negative output ({\tt BPB}) \\ \bottomrule
	\end{tabular}

	\caption{Pin connections for the output}
	\label{tab:output_pins}

\end{table}

\begin{wrapfigure}{l}{0.3\textwidth}
\centering
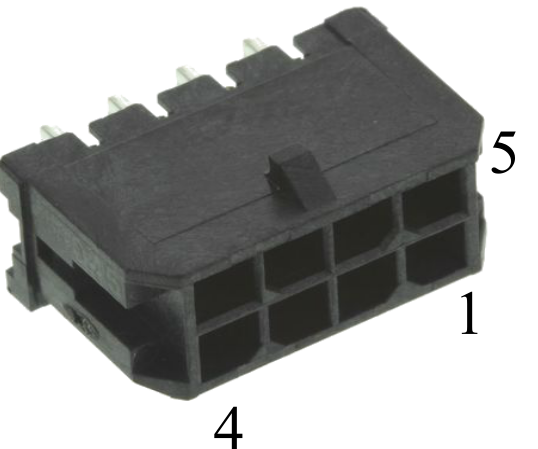
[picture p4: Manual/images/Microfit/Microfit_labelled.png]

\caption{Molex MICRO FIT 3.0 series 43045 output connector}
\end{wrapfigure}

The output connector is a Molex MICRO\_FIT 3.0 series 43045. It has 8 contacts, 4 of which are the OPA outputs and 4 are GND. In unipolar operation the device to be controlled (hereafter the plant) should be connected to one of the channels and GND. For bipolar operation connect to both the OPA output channels and leave the GND pins unconnected. 

\clearpage
\section{Thermistor input}

\begin{wrapfigure}{l}{0.3\textwidth}
\centering
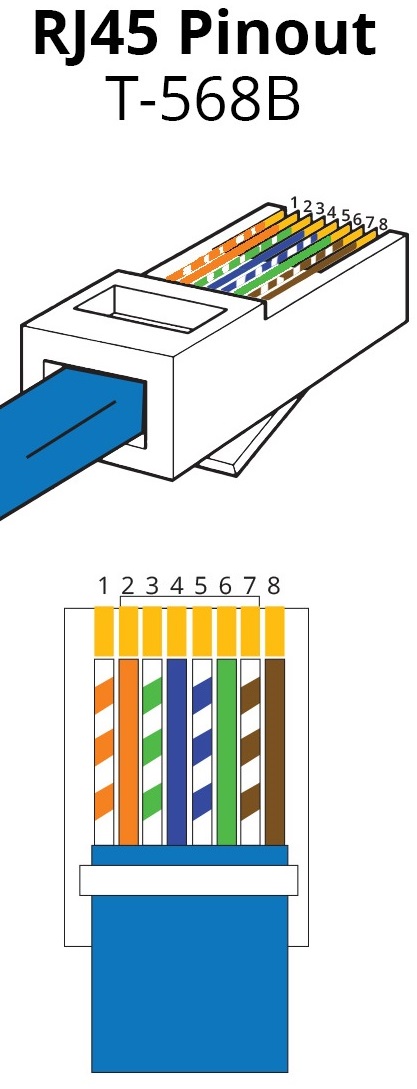
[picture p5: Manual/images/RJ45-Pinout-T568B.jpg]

\caption[Pinout for a RJ45 T568-B connector]{Pinout for a RJ45 T568-B connector \protect\footnotemark}
\end{wrapfigure}

\footnotetext{Image from \url{http://blog.showmecables.com/rj45-pinout/}}

\begin{table}[H]
	
	\centering

	\begin{tabular}{rll}
	\toprule
	Pin & Common colour & Purpose  \\ \midrule
	1   & Orange and white & GND      \\
	2   & Orange & Set resistor 1 +      \\
	3   & Green and white & GND	   \\
	4   & Blue & Thermistor 1 + 	   \\ 
	5   & Blue and white & GND      \\
	6   & Green & Set resistor 2 +      \\
	7   & Brown and white & GND      \\
	8   & Brown & Thermistor 2 +      \\
	\bottomrule
	\end{tabular}

	\caption{Pin connections for the error signal input}
	\label{tab:input_pins}

\end{table}

The error signal is produced by an INA330 chip that places a \SI{\VExcite}{\volt} excitation voltage ($V_{excite}$) across both a thermistor ($R_{therm}$) and a set resistor ($R_{set}$) and measures the difference in current. The signals in the RJ45 connector should therefore be connected to a thermistor and the set resistor. If an on-board set resistor is in use (see Section~\ref{sec:setpoint_resistors}) then the setpoint resistor pin on the input connector should be left floating. 

The RJ45 connector accepts standard Ethernet-style cat5 cable. This contains 4 twisted pairs, each of which is assigned to a channel. Table~\ref{tab:input_pins} assumes the standard T568-B colour scheme for RJ45 mounted CAT5 cable (orange, blue, green, brown: solid and dotted). 

\clearpage

% \section{Voltage input}

% \todo{Write something here}. Stuff. 

\section{Switches} % (fold)
\label{sub:switches}

There are two switches present on the board:

The vertical switch, {\tt COMMS\_DISABLE} can be used to disable / enable updating of the controller via USB connection. When this is set to disabled, all functions that alter the state of the controller will be prohibited (monitoring commands still work). When set to enabled, the controller functions as normal. This is intended to prevent accidental pertubation of a system under control. 

The horizontal, momentary switch {\tt RESET} causes a complete system reset.\footnote{Pressing this switch is actually not strictly equivalent to a power cycle as it does not reset the ADC. However, in the initial setup section of the software the ADS is reset via its SPI interface, so these two methods should give identical results.}

% subsection switches (end)

\section{LEDs}

The two front-mounted LEDs indicate the status of the lock(s) in progress. The LEDs are unlit if the device is currently outputting a constant voltage. If attempting to perform a lock, the two LEDs display the current distance from the setpoint of the lock controlling their respective control channels. A solid light means that the error signal is less than \SI{0.01}{\volt}, a slow flash means between  \SI{0.01}{\volt} and  \SI{0.1}{\volt} and a quick flash means greater than  \SI{0.1}{\volt}. These threshold values are defaults but can be altered over the serial connection (see Appendix~\ref{chap:available_commands} for a full listing of available commands). 

Locks are indexed as follows:

\begin{table}[h!]
	
	\centering

	\begin{tabular}{ll}
	\toprule
	\textbf{LED} 	& \textbf{Output channel} 		\\ \midrule
	1		&	1					\\
			& 	2					\\
			& 	BPA					\\ \midrule
	2		& 	3					\\
			& 	4					\\
			& 	BPB					\\ \bottomrule
	\end{tabular}
	\caption{LED assignments}
	\label{tab:led_assignments}
\end{table}

\section{USB}

The USB interface takes a micro-USB cable, allowing for monitoring and control over the system. The interface is isolated from the rest of the board to prevent ground loops. 

Communications are handled by a FTDI USB - serial interface IC which presents itself as a virtual COM port. Communication is then done via serial commands at a baud rate of \baudrate. See Appendix~\ref{chap:available_commands} for more info on commands accepted. 

% \section{Backplane}
% \label{sub:connectors_backplane}

% The optional backplane allow for rack mounting of the device. Power is taken from the \SI{24}{\volt} rail and regulated down on-board to power the micro controller and other electronics. 

% The backplane also supplies an RS485 interface to the micro controller. This is currently not implemented in software but could allow control of the whole rack by a single USB connection. 

% section connector_pins (end)

\chapter{Options and Hardware Configuration} % (fold)
\label{sec:options_and_hardware_configuration}

There are various points at which the board can be customised for a particular use case. Each section indicates default choices that will result in sensible behavior and are pre-installed on the boards. 

The file {\tt Pins.h} contains the descriptions of these customizations. If changes are made to the default settings, the user must alter this file and re-flash the device to reflect the changes, as described in Section~\ref{ssec:Pins}. 

% \section{OPA Choice} % (fold)
% \label{sub:opa_choice}

% Output can be powered by either OPA548 or OPA549 chips. The datasheets of the two devices detail their respective capabilities but, broadly, the OPA549 is more capable but bulkier and more expensive. 

% The 549 series are basically bigger brothers of the 548s: they can handle higher voltages, higher currents and higher temperatures safely with no loss in bandwidth or accuracy. 

% The OPA548s do have a couple of advantages however:

% \begin{enumerate}
% 	\item They are smaller and do not require an additional heat-sink since they are heat-sunk to the ground plane. 
% 	\item Both devices can have arbitrary current limits set in addition to software limits on output voltage. However the OPA549's current limit becomes inaccurate for limits of less than \SI{1}{\A}. The OPA548 can accurately limit currents right down to \SI{0}{\A}. 
% \end{enumerate}

% Applications requiring currents less than \SI{1}{\A} can probably get away with using the OPA548 devices. These are heat-sunk to the ground plane and have a low profile.

% In contrast, the OPA549s stand vertically around \SI{3}{\cm} above the board. If these are chosen, an appropriate heat sink should also be used (e.g. the RS 722-6915) which will increase the board profile to around \SI{4}{\cm}. However, these chips are capable of handling greater currents and operating safely at higher case temperatures. 

% Both devices incorporate internal thermal shutdown circuitry and so will not be damaged by overload conditions. 

% Use Figure~\ref{fig:OPA_SOA} to determine which device you should choose. The power dissipated by the OPAs depends on the difference between the voltage supply and the operational voltage. For example, if the supply voltage is \SI{15}{\volt} and \SI{5}{\volt} of output is requested, the OPAs will have to dissipate a \SI{10}{\volt} voltage drop across them. Depending on the current supplied, this can result in a considerable power. The power supply voltage and opamp family should therefore be chosen bearing in mind the intended output voltage and current of the device, with reference to Figure~\ref{fig:OPA_SOA}. 

% \textit{Default: OPA549}

\section{OPA Choice} % (fold)
\label{sub:opa_choice}

The four channel version of this temperature controller only has the option for output via OPA548. These are compact devices, heatsunk to the ground plane and capable of monitoring for thermal overload and accurately limiting current down to \SI{0}{A}. 

Figure~\ref{fig:OPA_SOA} shows the output currents that these devices are capable of. The power dissipated by the OPAs depends on the difference between the voltage supply and the operational voltage. For example, if the supply voltage is \SI{15}{\volt} and \SI{5}{\volt} of output is requested, the OPAs will have to dissipate a \SI{10}{\volt} voltage drop across them. Depending on the current supplied, this can result in a considerable power.

\textit{The power supply voltage and opamp family should therefore be chosen bearing in mind the intended output voltage and current of the device, with reference to Figure~\ref{fig:OPA_SOA}. }

\begin{figure}[tb]
	\centering
	
	\caption{Safe Operating Area (SOA) for the OPA devices. $V_S$ and $V_O$ are the supply voltage and output voltage respectively. For the OPA549, this assumes the use of the heat-sink recommended. Diagram adapted from the OPA548 and OPA549 data-sheets. The OPA549 is not available with the 4 channel board option. }
	\label{fig:OPA_SOA}
\end{figure}

% subsection opa_choice (end)

\section{OPA gain} % (fold)
\label{sub:opa_gain}

The DAC outputs voltages ranging from \SI{0}{\volt} to \SI{2.5}{\volt}. These are amplified by the OPA opamps to reach the desired output voltages. The choice of gain resistors R12 to R19 set the gain of this amplification and therefore the maximum possible output voltage using the formula:

\begin{equation}
\label{eq:OPA_Gain}
G = \frac{Rx + Ry}{Rx} \implies
V_{max} = \frac{Rx + Ry}{Rx} \times \SI{2.5}{\volt}
\end{equation}

\textit{Default: \SI{100}{\kilo\ohm} and \SI{500}{\kilo\ohm}, gain = 6x, $V_{max} =\SI{15}{\volt}$}

\section{Instrumentation gain}

The input current sensing chips work by current through a gain resistor to match the current difference between the thermistor and set resistor they are measuring, as described in Section~\ref{sub:ina330_thermistor_amplifier}. The choice of resistors $R_{gain1}$ and $R_{gain2}$ therefore set the range of inputs that are available. 

For precise sensing near the setpoint, a large gain should be chosen. However, in order to make possible a wide range of inputs, a smaller gain is appropriate. If you choose to alter the default gains, you must ensure that both $R_{gain1}$ and $R_{gain2}$ are the same and their values are updated in {\tt Pins.h} (see Section~\ref{ssec:Pins}). 

\textit{Default: \RGain{} giving a \tempRange{} temperature sensing range}

\section{Setpoint resistors}
\label{sec:setpoint_resistors}

For applications that do not require extreme stability, it is possible to place the set resistor on the board in footprints $R_{prec1}$ and $R_{prec2}$. If this is done, the external precision resistor connections should not be made.

Although it is possible to lock to arbitrary resistance values, various advantages are gained by operating at the point where $R_{thermistor} = R_{set}$. In particular, operating at this point means that noise in the voltage reference or EMF noise from other sources will not affect the setpoint. Also, for small values of $V_{out}$ the device will increase the gain of the input stage of the ADC, allowing greater sensitivity. 

Again, for less demanding applications this is unnecessary: on-board precision resistors and digitally defined setpoints will provide sufficient resolution.

% \todo{Quantize resolution loss with on-board resistors}

\textit{Default: \RSet{} on-board resistors}

\section{Sensing series resistors}

Unfortunately, the INA330 instrumentation amplifiers struggle to drive even modest capacitive loads, such as that presented by \SI{30}{\cm} of BNC cable. For this reason a \SI{1}{\kilo\ohm} resistor is necessary in series with the thermistor and precision resistor to prevent bias voltage oscillations.

For the most demanding applications this series resistor can be removed and replaced with a piece of wire, reducing sensitivity to board temperature but necessitating short wires to the thermistor / set resistor. 

\textit{Default: \RSeries{} precision resistor}

\section{Pins.h}
\label{ssec:Pins}

Once customisation options have been chosen, the user must re-flash the device with a version of the source code reflecting these choices. To do this, the file \texttt{Pins.h} should be updated with the changes made and then the software should be compiled and uploaded using e.g. the Arduino IDE. Remember to temporarily re-enable flashing by using the vertical switch on the front panel. 

% section options_and_hardware_configuration (end)

\chapter{Initial setup} % (fold)
\label{sec:initial_setup}

The procedure for setting up a board is therefore as follows:

\begin{enumerate}
	\item \textit{Optional: Choose what configuration you require in accordance with Section~\ref{sec:options_and_hardware_configuration}, or accept the defaults.}
	\item \textit{Optional: If you chose to customize your board in the previous step, make these modifications now. }
	\item \textit{Optional: Open the {\tt Pins.h} file in the MC software folder. Edit it in accordance with your choices or leave it at defaults. (See the Doxygen documentation (Appendix~\ref{chap:full_doxygen_documentation}) for an in-depth description of each option)}

	\item Solder the OPA drivers you chose to the board if using the single channel board. The dual channel board comes pre-populated. 

	\item Using Atmel Studio and an AVRISP mkII programmer, connect to the ISCP header on the board and 

	\begin{enumerate}
		\item Set the fuses to:
		\begin{verbatim}
			low_fuses=0xff
			high_fuses=0xde
			extended_fuses=0x05
		\end{verbatim}
			
		\item Upload the Optiboot boot-loader file \path{./Code for Microcontroller/optiboot_xplained328p.hex} to the flash memory. 
	\end{enumerate}
	These steps only have to be performed once per microprocessor. The board must be powered during this step. 
	
	\item Using the Arduino IDE, compile and upload the code to the device. After this is done, remember to re-enable flashing using the {\tt FLASH\_DISABLE} jumper. 
	
\end{enumerate}

After this process is complete, the device will appear over USB as a COM port. In order to test that everything went well, send the command {\tt *TST} (at baud rate \baudrate). If the response ``OK" is received, the software is installed correctly and communication between the microprocessor and the ADC is working. 

\todo{*TST not currently implemented}

% section initial_setup (end)

\chapter{Voltage Conversion Formulae} % (fold)
\label{sec:voltage_conversion_formulae}

The readings output by the device will be in volts, whereas usually the user will be interested in determining the resistance of a thermistor. For more details about how this voltage is produced, see Section~\ref{sub:ina330_thermistor_amplifier}. The voltage output $V_{out}$ is the voltage produced by the INA330 instrumentation amplifier according to its gain resistor $R_{gain1}$ or $R_{gain2}$. To convert this to a resistance, you must know the resistance of the set resistor (default $R_{set} = \RSet$), the excitation voltage ($V_{excite} = \SI{\VExcite}{\volt}$), the gain resistance ($R_{gain} = \RGain$) and the series resistance (default $R_{series} = \RSeries$). Use the following formulae:

\begin{equation}
\label{eq:volt_to_resistance}
R_{therm} = \left[ \frac{1}{R_{set} + R_{series}} - 
	\frac{V_{out}}{V_{excite} . R_{gain}} \right] ^ {-1}
	- R_{series}
\end{equation} 

or

\begin{equation}
\label{eq:resistance_to_voltage}
V_{out} = V_{excite} R_{gain} \left[ \frac{1}{R_{set} + R_{series}} - \frac{1}{R_{therm} + R_{series}} \right]
\end{equation} 

Thus, close to the set point, i.e. for small values of $V_{out}$, $V_{out}$ is linearly related to resistance. 

% section voltage_conversion_formulae (end)

\chapter{Hardware Design} % (fold)
\label{sec:hardware_design}

The board is designed to be rack-mounted with dimensions of $\SI{100}{\mm} \times \SI{80}{\mm}$. It is compatible with IEC 60297-3/-4 specs regarding dimensions and can fit front panels such as e.g. RS 258-2920. 

% This corresponds to half Eurocard format with an additional \SI{20}{\mm} added to provide space for the backplane connection. If this connection is not required it can be removed from the board (either at the printing stage or with a saw!) without impacting upon the rest of the board. \todo{Make Eurocard chopping possible}

\section{Isolation}

Since the error signals read by this board are at DC, much care was taken to avoid ground loops and crosstalk that could introduce bias. The ADC described in Section~\ref{sub:ads1262_analog_to_digital_converter} implements various filtering methods, but the board is also designed to prevent extraneous noise. 

The USB input interface is opto-isolated from the rest of the board, with power for the FTDI USB chip provided by the computer host. Also the entire analog section; incorporating the ADC, instrumentation amplifiers and input opamps; is isolated from the rest of the board and powered by a DC-DC converter. 

Although the output stages are not isolated from the rest of the board due to their high power requirements, care has been taken to manage high frequency digital return current in order to avoid signal crosstalk. The board has internal ground and power planes to reduce EMI and these both contain a bottleneck at the DAC: the point at which digital signals end and analog signals begin. This design is intended to keep digital return currents within the digital section of the board, avoiding pollution of the output stages. 

\begin{figure}[h!]
	\centering
	
	\caption{Segmentation of the 2 channel board for isolation and ground loop considerations. 4 channel board is similar}
	\label{fig:isolation}
\end{figure}

\section{ADS1262 - Analog to Digital Converter} % (fold)
\label{sub:ads1262_analog_to_digital_converter}

The ADS1262 is a nominal 32-bit ADC produced by Texas Instruments. During a temperature reading it is configured to use a two stage digital filter. The first order provides a fixed 5th order sinc filter. The second stage is a programmable order sinc filter, set to 4th order. These two together result in an \SI{0.58}{\Hz} \SI{-3}{\dB} bandwidth, with poles at \SI{50}{\Hz}. On top of this, a simple analog external RC low-pass filter prevents aliasing. 

The ADS1262 has inherently low input offset bias however, to combat any residual bias, every measurement is taken twice with the input signal paths swapped over via the internal analog MUX. 

The IC also contains an optional Programmable Gain Amplifier (PGA) stage. The micro controller monitors the signals it reads and, if it detects several measurements in a row that would have benefited from increased gain, it automatically boosts the gain stage to increase sensitivity further. If the signal later becomes too large for the gain selected this is also automatically detected and corrected by the micro controller. 

Because of this re-sampling and filtering, a single measurement can take up to \SI{5}{\second} to complete. Programs that interface with the temperature controller should therefore be aware that commands such as {\tt ERRO? 1t} can take up to \SI{5}{\second} and should take appropriate steps to avoid timeout. The Labview interface handles this automatically. 

\begin{figure}[h!]
	\centering
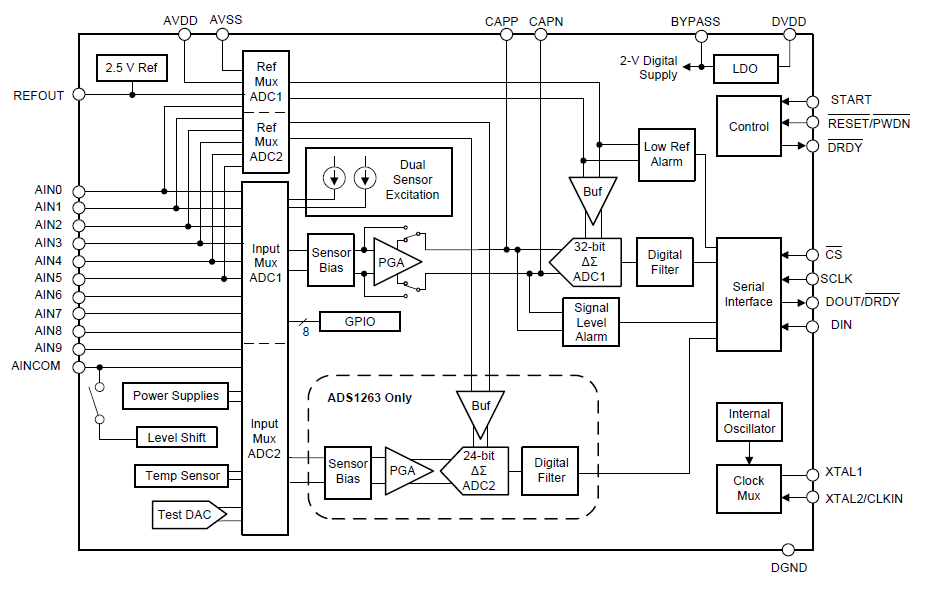
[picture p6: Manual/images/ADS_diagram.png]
	
	\caption{Flow diagram of the ADS1262. Reference: ADS1262 datasheet by Texas Instruments}
	\label{fig:ADS_Flow}
\end{figure}

% subsection ads1262_analog_to_digital_converter (end)

\section{INA330 - Thermistor Amplifier} % (fold)
\label{sub:ina330_thermistor_amplifier}

\begin{figure}[tb]
	\centering
	
	\caption{Flow diagram of the INA330. The \SI{2.5}{\volt} reference comes from the ADC and the output voltage is refereed to this reference. The \SI{\VExcite}{\volt} excitation reference is derived from the \SI{2.5}{\volt} reference ratiomatically for maximum common-mode rejection. Diagram adapted from INA330 datasheet by Texas Instruments.}
	\label{fig:INA_Flow}
\end{figure}

The thermistor / setpoint precision resistor comparison is done by an INA330 chip. These chips take a reference voltage, \SI{\VExcite}{\volt} on this board, ratiomatically derived from the stable \SI{2.5}{\volt} reference of the ADS1262. This is buffered and used to drive both the thermistor and the resistor. The current difference between these two arms is then forced through a gain resistor, $R_{gain1}$ or $R_{gain2}$ (by default \RGain), amplifying it with respect to the \SI{2.5}{\volt} reference. This signal is then read by the ADC and compared to the \SI{2.5}{\volt} reference in differential mode. 

Figure~\ref{fig:INA_Flow} shows a schematic of the INA's operation. 
For a resistance to voltage conversion formula use Equation~\ref{eq:volt_to_resistance}.

% subsection ina330_thermistor_amplifier (end)

\section{OPA548/9 - Output Amplifiers} % (fold)
\label{sub:opa548_9_output_amplifiers}

The final output to the plant is handled by an OPA548. These amplify the $\SI{0}{\volt} \rightarrow \SI{2.5}{\volt}$ signal produced by the DAC to the voltage required by the user, set by gain resistors as described in Section~\ref{sub:opa_gain}.

% subsection opa548_9_output_amplifiers (end)

\section{DAC8564 - Digital to Analog Converter} % (fold)
\label{sub:dac8564_digital_to_analog_converter}

The production of the analog signal is done by the DAC8564: a 16-bit digital to analog converter, referenced to its own internal \SI{2.5}{\volt} reference. 

Its output ranges from \SI{0}{\volt} to \SI{2.5}{\volt}. This signal is then either amplified by the OPAs to become the output level, or doubled by a AD8639 auto-zeroing opamp to control the current limiting feature of the OPAs. 

% subsection dac8564_digital_to_analog_converter (end)

\section{ATMega328p - The micro controller} % (fold)
\label{sub:atmega328p_the_micro_controller}

The brain of the device is an ATMega328p MC. This is the same processor that is found on the Arduino Uno or Nano, and the board is configured (instructions in Section~\ref{sec:initial_setup}) to appear as an Arduino Nano to the computer. However, by breaking the Arduino into pieces several advantages are gained including reduced board space and the option to add on-board isolation to the USB interface. 

The ATMega is clocked from a \SI{16}{\MHz} full-swing crystal. When the board is assembled for the first time the ATMega's flash memory will be blank and the device with not be programmable over the usual USB interface. For the first time only, programming must be done by the ISCP header provided, as described in Section~\ref{sec:initial_setup}. 

% subsection atmega328p_the_micro_controller (end)

% \section{Backplane} % (fold)
% \label{sub:hardware_backplane}

% The board is also equipped with an optional DIN41612 backplane connector, RS number 252-210. If used, the board draws its power from the 24V rail of the backplane and must not be powered from the front panel. 

% Connecting the backplane also enables RS485 communication. Although the software for this has not, at the time of writing, been developed, this hardware layer in combination with the Modbus protocol should enable easy, collision-free control of an entire rack of devices using a single USB connection. 

% subsection backplane (end)

\section{RS485} % (fold)
\label{sec:rs485}

The board is equipped with a 4 pin Molex PicoBlade 53048-0410 connector that enables RS485 communications. This is currently unimplemented, but will allow for control of up to 255 RS485 boards from a single USB connection. 

% section rs485 (end)

% section hardware_design (end)

\chapter{Software Structure} % (fold)
\label{sec:software_structure}

The code running on the micro-controller is written in C++. The ATMega328 is set up to appear the same as an Arduino Nano: it is therefore possible to compile and upload the code using the usual Arduino IDE. Note that re-flashing like this this requires two things: a) the {\tt FLASH\_DISABLE} switch should be set correctly (see Section~\ref{sub:switches}) and b) the boot-loader must have been installed using the ISCP header (see Section~\ref{sec:initial_setup}). 

The code-base makes considerable use of the object-orientated programming style. While this can appear daunting at first, in the long run it simplifies modifications and results in more compartmentalized code that is easier to understand. This overview and the more in-depth Doxygen documentation both assume some familiarity with concepts such as virtualisation, inheritance, abstraction and polymorphism.

There are very many online and offline resources that can give you an overview of these ranging from 1 page to multiple-volume books. For a quick starting point, try \url{https://www.cs.bu.edu/teaching/cpp/inheritance/intro/} and \url{https://www.cs.bu.edu/teaching/cpp/polymorphism/intro/}. 

\section{Doxygen} % (fold)
\label{sub:doxygen}

The code is thoroughly commented throughout to aid comprehension. These comments have been written to comply with the requirements of the documentation program Doxygen \url{http://www.stack.nl/~dimitri/doxygen/}. It is therefore simple to compile all these comments into a manual by installing the Doxygen program on your computer, launching the wizard, selecting the {\tt Doxyfile} file in the temperature controller's source code and running the wizard. This will produce a neatly linked set of HTML files that can be opened in any browser. It will also produce \LaTeX{} output, the result of which is appended to this document in Appendix~\ref{chap:full_doxygen_documentation}. 

The Doxygen output is detailed and should be considered the authority if modification to the code is required, but this section provides an overview of the code structure. 

% subsection doxygen (end)

\section{Code Overview} % (fold)
\label{sub:code_overview}

As per usual object-orientated design, the jobs performed by the temperature controller are split between objects. Two of the most important are ErrorChannels and CtrlChannels. These classes manage interactions with the world. They are abstract classes, and provide a template of functions which must be fulfilled by their derived classes. 

For instance, CtrlChannels have a method setCtrl() which sets the output voltage available at the OPA. This method takes a double as a parameter, the new control level, which adheres to a convention used throughout the code: all error readings or control outputs are given as a number between -1 and +1 where -1 corresponds to the lowest possible level and +1 corresponds to the highest. 

A specialisation of CtrlChannel is V4\_OPA\_OutputChannel. This overrides the ``pure virtual'' methods in CtrlChannel and writes a voltage to the output channel it manages. On initialisation this object is assigned to one of the OPAs. A value of for output -1 would correspond to 0V, a value of +1 would be {\tt +MAX\_VOLTAGE} V. 

A different specialisation of CtrlChannel is V4\_OPA\_OutputChannelBipolar. This object also performs output, but rather than outputting a voltage on a single OPA, it uses 2 OPAs at the same time in order to output a bipolar differential level. 

ErrorChannels have similar functionality but are used for input instead of output. However, since taking a reading can take several seconds (see Section~\ref{sub:ads1262_analog_to_digital_converter}) there is a bit more structure involved. Readings are initiated with startReading(). Before this happens, the calling code should check that no reading is already in progress by calling globalReadInProgress(). Once a reading has been started, its progress can be checked by calling readingReady() and then its result can be output using getReading(). 

Other important objects in the code are:

\begin{description}
	\item[Controllers]  Contain references to an ErrorChannel, a CtrlChannel and an Algorithm. Every time doLoop() is called, attempt to take a reading from the ErrorChannel, process it with the Algorithm and output it with the CtrlChannel. 

	\item[Algorithms] An abstract class that defines an object responsible for processing an input error signal and returning the new control level. This object should contain information about the set-point and any limits applied. An example implementation is PIDAlgorithm. 

	\item[CommandHandler] An independent object that can be included as an Arduino library in any project. This object manages the input and parsing of serial commands. It uses a hashing algorithm to minimize memory consumption and assigns all memory on the stack to avoid fragmentation. It is responsible for calling the appropriate function when a command is issued. See its own Doxygen documentation for much more detail. 
\end{description}

A typical cycle in the code looks like this:

\begin{enumerate}
	
	\item Check CommandHandler for new commands and execute them if present. 
	\item For all Controllers, see if a lock is in progress
	\item If so:
	\begin{itemize}
	 	\item If an ADC reading is in progress do nothing. 
	 	\item If no reading is in progress, start one. 
	 	\item If an ADC reading for this channel is complete, get the result and move to step 4. 
	 \end{itemize} 
	\item Feed the result of the reading into the contained Algorithm
	\item Get the new control level back from the Algorithm and pass this to a CtrlChannel for output. 

\end{enumerate}

% subsection code_overview (end)
% section software_structure (end)

\clearpage
\begin{appendices}

% \chapter{Todo list} % (fold)
% \label{sec:todo_list}

% % Hack to get todonotes to work with amsart
% \makeatletter
% \providecommand\@dotsep{5}
% \makeatother

% \listoftodos\relax

% section todo_list (end)

% \chapter{Known bugs} % (fold)
% \label{sec:known_bugs}

% section known_bugs (end)

% \chapter{Git} % (fold)
% \label{sec:git}

% \todo{Write git appendix}

% section git (end)

% \clearpage
% \chapter{What is Object Oriented Programming?} % (fold)
% \label{sec:the_object_paradigm}

% \textit{
% The following essay was written by Andrew Hardwick and released under the GPL license at \url{http://duramecho.com/ComputerInformation/WhatIsObjectOrientedProgramming.html}. This is a verbatim copy.
% It is intended as a quick introduction to the principles and benefits of Object-Orientated Programming (OOP). The target reader will have familiarity with programming concepts such as methods, variables, arrays but needs no knowledge of OOP. 
% }

% \section{Firstly: Don't Panic!}

% Object Oriented Programming (called `OOP' for short) is promoted as a radical, difficult to comprehend \& even frightening way of programming that vital to know about. Is this true? No.

% Object Oriented Programming is not very radical or very difficult compared to conventional programming. When one looks under the ideology and sees what is actually there, one finds there is not really much different at all!

% The reason for it seeming so difficult is that introductions to OOP are normally given by the follow types of people who are not ideal for teaching the basics:

% \begin{description}
% 	\item[OOP Zealots] These advocate OOP in seminars \& articles with great enthusiasm but leave the audience with little understanding of what OOP actually is, just a feeling that it is revolutionary \& complicated. The dogmatic fervour scares people off.

% 	\item[Computer Scientists] These marvel in lectures about the structures and relationships that an object oriented approach can bring and draw lots of rectangles, lozenges or clouds joined by lines This is rather pointless as it is all fairly obvious to the mathematically minded in the audience and is all totally incomprehensible to the rest. The boredom puts people off.

% 	\item[Programmers] These helpfully give the details of how to do particular things in particular OOP languages in web pages \& books but miss out the basic introductory explanations. The detail puts people off.
% 	\item[Incompetents] Unfortunately there are some of these. I've even come across a lecturer from a London university who was paid to teach us OOP but could not answer the first trivial question when challenged to explain the rhetoric. The confusion puts people off.
% \end{description}

% In the following article I will try to explain what OOP is and why it is used but without the customary hype, irrelevant extras \& detail (and, hopefully, without the incompetence). I am assuming the reader is familiar with the fundamental concepts of normal programming such as a program being made of `commands' which tell the computer do things, `variables' to store data in and the idea of grouping a set of commands together in `functions' (or `subroutines' which are virtually the same) which can be called as needed from different parts of a program. However, the ability to write programs is not required and I won't be giving the detailed syntax for any particular OOP language. If you want that then there are a surfeit of books \& web pages to choose from already.

% \section{What Object Oriented Programming is}

% Firstly, some background. A conventional (`procedural') program consists of a sequence of commands. The commands can do input, output, manipulate data and control the order in which the commands are carried out. So as not to have to duplicate commands in different places in a program where same action needs to be performed, a set of commands can be combined into a `function' or `subroutine' which acts like a new command. This same set of commands can then be called from different places in the program. As well as substantially reducing the length of programs, this can make the structure neater by encapsulating the commands which, together, perform some particular operation in one place. The rest of the program need not be concerned about the details of what commands make up the function and just treat it as something which does that operation. This neatness is not merely an aesthetic feature but a great aid to making programs quicker to write, easier to debug, more reliable \& more reusable.

% Splitting a program into functions makes programming quicker not only because different programmers may be able to work on separate functions at the same time but, crucially, it breaks down a huge task which would be difficult for a human to store in mind as one piece into smaller units more suited human memory. It makes debugging easier because it localises the effect of a single bug so it is easier to track down and, when bugs have been eliminated from a function, one need not waste time rechecking it when debugging other parts of the program. To aid this, it is normal to have the variables a function uses internally hidden from the rest of the program, unless there is a special necessity to reveal them. This ensures that any problem related to such a `local' variable can be traced to function which needs correcting. This also makes the program more reliable because, once a function is working, it should stay working as more of the program is built up. Other parts of the program cannot disrupt those hidden variables \& commands inside the function. The splitting also, of course, makes subsequent programs quicker to write as whole functions can be reused from earlier programs and even stored in libraries for use by any future program. The generic term for this is approach of breaking a big solution into small pieces whose internal workings are not of concern to other pieces is `modular'.

% Enough about functions. Now for variables. In many computer languages, a programmer can define a compound variable type in addition to those which are ready made in a language. For example if a particular language has variable types for names \& dates, a type for storing birth records could be made by combining two name type variables, for the family name and given names, with a date type variable, for the date of birth. These combined variables are called different things in different languages including `structures' (C), `clusters' (LabView) \& even just `types' (Fortran). Combined variable types can be useful. For example, instead of having to work on and pass around three variables together whenever a birth record is used, a single variable of this combine type could be thus be used. Commands \& functions which don't need to use all the member variables of a combined variable need not be concerned they are there. One can even copy a combined variable in one command, rather than one command for each member variable, without knowing or caring what all the member variables are. This is applying a modular approach to collections of variables as functions were for collections of commands.

% That was around for decades then someone then came up with the idea of including functions as well as variables in those combined variable types. Combined variable types could then have member functions as well as member variables. These functions are only really in the program once (it would be very inefficient otherwise) because they are written into the variable type specification not the individual variables of that type themselves. However, they act as if they were duplicated in each variable of that combined variable type because they, by default, act on the member variables of the particular variable of the variable they called with. For example one could have included a member function to calculate a person's age into that birth record combined variable type. When a particular variable of that type, storing a particular given name, family name \& date of birth, has its age calculating member function called, the function will automatically use the member variables of that particular variable, not the generic variable type, to calculate an age. This can be quite handy because it neatly bundles data \& the functions which act on it together. It can also aid conceptualising a program because, in calling a member function, one is effectively telling the data what to do to itself which is, in some situations, closer to reality than giving the data to a command to process.

% Now you have understood that, we can go onto Object Orientated Programming at last. Correction: if you have understood then you have understood Object Oriented Programming! That idea in the preceding paragraph of putting functions into combined variable types is Object Oriented Programming! Does it not sound dramatic enough? Okay, lets put some hype in: rename 'member functions' to `methods'; rename 'combined variable types' to `classes'; and rename 'variables of combined types' to `objects'. That's all it is!

% \section{A Few Little Extras}

% There are few useful extras which normally come with OOP. They can mostly exist in procedural programming languages as well so they are not necessarily OOP features but they are ubiquitous in OOP languages so I suppose I ought to mention them. You can skip this section if it is too detailed.

% \begin{description}
% 	\item[Data hiding] Just like functions can have local variables not visible to the rest of the program, so can objects. This is for storing data that is not revealed or set directly but only via methods (member functions). For example a birth record object could store the year, month \& day of birth in separate member variables and only combine them when asked for date of birth by a method call. Some OOP advocates even recommend that all member variables are hidden and only accessed via methods but that is sometimes excessive.
% 	\item[Automatic initialisation] A class can have a method (called a `constructor') which is automatically called whenever a new object of that class comes into being. This like having a default value for a variable type that a variable is initialized to when it is created prior to being set. However, as objects have member functions (methods) as well as member variables, this has been generalised into a method call that can do a lot more than just set a default value. There is a corresponding method (called a `destructor') which is called when an object is disposed of and is typically used for clearing up.
% 	\item[Same name, different function] Different functions can have the same name provided they are distinguished by their parameter types. This is useful in procedural languages but is almost vital in OOP languages because classes may come with functions that take objects of the class as parameters (as well as member functions embedded in the class) and it likely that there will be a duplication of popular function names between classes from different programmers. In OOP, this ability to have multiple functions with the same name is called `overloading'.
% 	\item[Derived classes] If one requires a class which like a class one already has but requires extra features then one can derive a class from an existing class. The derived class has all the externally visible methods \& member variables the base class it was derived from had (and, optionally, some of the hidden ones) plus whatever extras are put in. For example one could derive a class from birth record class that also a member variable for time of birth or a method for combining the family \& given name into a full name. Besides aiding reuse of program parts, it is possible to have different derived classes from the same base class for slightly different situations. For example British \& Chinese versions of the previous example could be made where the British one calculates a full name by appending the family name to the given name whereas the Chinese one joins them the other way around. A nice feature of this is that objects of both types could then be stored and processed the same (thereby saving programming) and yet perform differently when the full name method is called. In OOP, this ability to have the same function perform different actions depending on the derived class is called `polymorphism'.
% \end{description}

% \section{Why it can be Good Thing}

% OOP is good for the same reasons that other modular programming schemes are: aesthetic neatness, quick writing, eased debugging, improved reliability \& increased reusability in large programs.

% In addition, an object based structure naturally fits certain common uses of computer programs including graphical user interfaces (with buttons, windows, scroll bars as objects) and databases (records as objects).

% Of course, all this the modular structuring can be done with a classical `procedural' language (indeed the OOP C++ language was originally made a collection of `search \& replace' operations that converted C++ programs to the procedural C language!) but looks cleaner in OOP because OOP was designed for this structuring. And OOP is fashionable!!

% \section{Why it can be a Bad Thing}

% There are drawbacks to OOP as well. It is not the best thing to use in all circumstances. Don't fall into the trap of using for ideological reasons when it is not the most suitable method for a particular task (and similarly don't dogmatically stick to a single programming language, pick the more suitable one for each job).

% For a start, it should be obvious that OOP, or any such heavy programming method, is probably not ideal for doing small quickly-written one-off programs where the time taken to define a class structure is more than the time you will save by having it neatly modular. Of course, one can use an OOP language for short programs, it is just that structuring your own programs in an OOP fashion in addition to using the language's in-built own objects would be inefficient. I don't know what the cross-over point is but I guess it is several hundred lines of program for myself, although I would probably do modular structuring into functions at well below a hundred lines.

% Neither is it suitable for very low power computers such as the microcontrollers embedded in consumer products which often have only less than a kilobyte of memory to fit the program into (compared to gigabytes on a office PC) and only a few bytes (compared to megabytes) to store variables in.

% There are also some jobs which are naturally ``do this ... then this ... then this ... then this ..." tasks in which case programming it procedurally could well be neater and easier than doing it object oriented. I've found this for simple one-task programs that control mechanical devices or batch process files. They typically read in the parameters, read in data from files, apply a series a manipulations to the data \& parameters and output to electronic hardware or to a file in that order. Sometimes they don't even have conditionals or loops. Object orientation would be an ill-fitting arrangement for these programs. (An interesting aside: often such small programs are called in turn by other small programs and a collection of such programs naturally builds up into an effectively object oriented system, where the little programs act as classes, without any planned intention for them to be so.)

% The most serious drawback is one common to all neatly structured modular programming: the division into modules really needs to be decided in advance of programming. In an ideal programming situation this would be the case but, in reality, customers who don't understand programming often change the requirements drastically after programming has been started (or even finished!). Often spec's are changed in a way that looks small from the outside but which mean that objects which were built to act totally independently of each other are changed so that they need to control eachother directly. The program alterations are then either a time-consuming restructuring of much of the program or messy ad-hoc direct links which wreck the modularity. For example, if a customer asked for a simple product database in which records are only ever set once \& recalled one at a time for reading, then the obvious class structure would be one of a records class for storing the product data and a database class consisting of an array of those customer records objects along with a method to add a new record object and search method to returns a copy of a requested record for reading. If the customer then demands that a product record should link to related products with the links changeable from the display terminal, then the structuring will be serious. Not only will it need that extra variable added to the record class (easy) but record objects will need to link to other record objects which was previously only via the database object (disrupts the neat modular structure), the database will need to pass around the original record object instead of a copy so it can be altered (lots of changes needed in different places in the program) and a contention-resolution system will be needed to prevent the records now being altered from different parts of the program simultaneously (a difficult and time consuming programming task). The only solution I know of for this is to warn customers that such spec' changing is like asking for different foundations in a house after the walls are built and get them to contractually agree to pay for such alterations they request but customers don't like that.

% \section{The Real Reasons that it is so Popular in C/C++!}

% The rest of this article was not language specific but one major misconception needs to be cleared up with the language`'C++'.

% OOP is most commonly advocated for `C++'. In part this advocacy is just because `C++' is the procedural language `C' with OOP added in later so they make a nice pair of languages to compare \& contrast unlike, for example, `Java' which was OOP from its first creation. However this does not explain the fanatical enthusiasm with which C++ was welcomed. Was the explanation that OOP was so much better than procedural programming? No. It was simply that there were some very useful things absent from the original C language that were either rectified in C++ or could be bodged up with OOP tricks:

% \begin{description}
% 	\item[Strings \& arrays] Almost amazingly, C does not really have variables of string or array type. Instead strings \& arrays have to be cumbersomely bodged in using pointers to general-purpose chunks of memory with the programmer having to maintain separate records of where they are \& how long they are and resort to tedious explicit memory cell copying operations to duplicate them or change their lengths. Although C++ does not come with strings or arrays either, one can write classes which encapsulate the memory manipulation routines and, at last, use instances of them as if they were intrinsic string \& array variables without further hassle. (Other than the hassle of there being many different string \& array classes and each product's library seems to use different ones which need interconversion! Even I have written my own ones after finding the ones that came with the MS C++ compiler were not fast, easy or reliable enough for my requirements.)
% 	\item[Memory deallocation] Despite C programming needing so much direct memory manipulation, it does not automatically free up memory when it is no longer needed like Perl \& Java do. Therefore the programmer must write their programs so that they tediously keep track of all memory that has been allocated by request and explicitly free it up when no longer needed. This is especially tedious where there are many ways a function can exit (such as after testing for different errors) and each one must have commands to free up the same memory. If this is not done then the computer runs out of memory as more \& more of it is left reserved but not actually in use (a situation so common that it has the been given the name of a ``memory leak"!). Although C++ still has this problem, it is slightly less hassle as one can create classes for the variables which need memory allocation, perform the allocation in the class's constructor \& free it up in its destructor so one only needs to program the freeing up in once instead of everywhere such a variable might cease being used.
% 	\item[Function overloading] It is annoying in C that if one wants to write a function that can process more than one type of variable then one has to give the functions different names and type the correct name for the data type when using it. For example one has to use `abs()' to calculate to the absolute (unsigned) value of an integer but `fabs()' to do the same thing for a floating point number. The compiler should be able to distinguish these itself from the type of parameter. In C++ it can. This is not a specifically OOP feature though.
% 	\item[Unspecified variable type] C likes to know what type its variables are even when the specific features of that type are irrelevant. This annoying when wants to store a collection of variables of different types in an array or write a program that will not need reprogramming when new types are added. The normal solution is to have duplicate commands for the different types or a messy ``void pointer" fudge. With OOP one can derive all ones variable types on one base class (even if that base class does absolutely nothing!) and treat them all as being of that type.
% 	\item[Localised namespaces] When writing a big program, it is difficult to ensure that names of functions are not duplicated in different files. This is especially a problem for little functions which need not be visible to other modules, just for use internally. A name like 'IncreaseCount()' could easily be accidentally duplicated. A common solution was to start each function name with the name of the file or module which it was in but that was messy, increased typing \& actually broke the official C spec' (which stated compilers could ignore all but the first 6 characters of function names). In C++ there is a neater bodge-up: bunging all the functions from one file or module in a class, even if that class does not have any variables, neatly localises the function names. Once more, this is need not have required OOP; for example, in the Perl language one can specify anything to be only locally visible (indeed adding OOP features to Perl required almost no changes to the language, essentially just an alternative syntax which called such localised regions classes!).
% 	\item[//] The most commonly used C++ feature, which is now used ubiquitously in programs which otherwise use only pure C commands, is the `//' command which merely means ``ignore everything else on this line"! It is quicker to type than the original C comment markers '/*...*/' which needed one to mark both ends of the stuff to ignore.
% \end{description}

% The reason for these deficiencies in C is because C was designed for low level fast programs on low power computers not for database \& graphical user interface programs on the far more powerful computers available at present. It is C++'s adaptation of C towards this changed role which gives it its popularity not so much its OOP nature.

% \section{Summary}

% Object Oriented Programming is not as different from normal procedural programming as is made out by its advocates and is not as difficult to understand as their proselytising implies. It is useful in making big modular programs but such programs should have been structured very similar to an OOP structure anyway. It can be more hassle than it is worth for short \& quick programs. The enthusiasm for C++ in particular is mainly because it adds in some important basic features that were missing from C.

% % section the_object_paradigm (end)

% section overview (end)
\chapter{Available Commands} % (fold)
\label{chap:available_commands}

The commands recognised by the controller are defined in the file \path{./Code_for_microcontroller/YbTempCtrl/CommandDefinitions.h} and the Doxygen documentation (Appendix~\ref{chap:full_doxygen_documentation}) for this file contains a complete list of them. 

This documentation is reproduced here for convenience. The following is automatically generated from the code's markup, so please excuse any odd formatting. All parameters should be separated by spaces. All commands must be followed by a newline (ASCII 10) character. 

\def\Hypertarget{{}}
\renewcommand{\Hypertarget}[1]{}
\input{../Code_for_microcontroller/YbTempCtrl/doc/latex/_command_definitions_8h.tex}

\chapter{Full Doxygen documentation} % (fold)
\label{chap:full_doxygen_documentation}

The following pages are the full documentation of the code, produced automatically by Doxygen. Doxygen is a code commenting system that allows you to write structured comments throughout your code which can later be extracted into a code reference.

To get the latest version of this reference, incorporating any changes, you need to install Doxygen, run the Doxywizard, load the file \path{./Code_for_microcontroller/YbTempCtrl/Doxyfile} and click ``Run doxygen''. This will produce HTML and \LaTeX{} output. 

It will also generate a file called \path{make.bat} in \path{./Code_for_microcontroller/YbTempCtrl/doc/latex/make.bat}. Execute this file to produce the updated \LaTeX{} code reference. To incorporate this into the manual you are currently reading, just recompile the latex from \path{./Manual/TemperatureControllerManual.tex}. 

\includepdf[pages={-}]{../Code_for_microcontroller/YbTempCtrl/doc/latex/refman.pdf}

% chapter full_code_documentation (end)

\end{appendices}

\end{document}

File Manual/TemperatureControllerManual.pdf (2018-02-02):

## Digital isolated 4 channel temperature controller

Version: v4.3D

Charles Baynham

February 2, 2018

# Contents

1 Overview | 3
2 Connector Pins | 5
3 Options and Hardware Configuration | 10

1

4 Initial setup | 14
5 Voltage Conversion Formulae | 15
6 Hardware Design | 16
7 Software Structure | 21
Appendices | 24
A Available Commands | 25
B Full Doxygen documentation | 31

2

## Section 1

# Overview

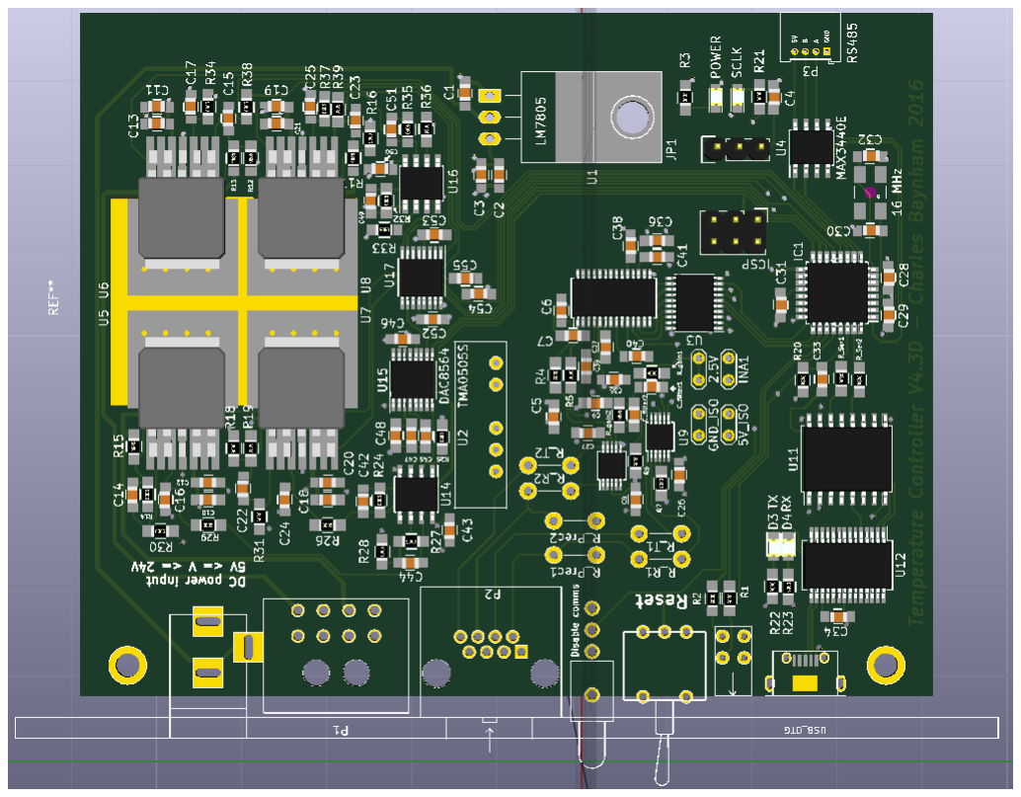
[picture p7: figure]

Figure 1.1: Picture / render of the board

This manual describes the operation and design processes behind the Yb⁺ digital temperature controller, version v4.3D. The controller is designed for taking high precision temperature measurements via a thermistor and applying low bandwidth PID feedback in response.

### 1.1 Microprocessor

The device is controlled by an on-board microprocessor running at 16 MHz. It operates in headless mode and can be configured to automatically recover from power failures.

3

Setup and monitoring is by USB connection, baud rate 57600. This USB connection is electrically isolated from the rest of the board to prevent ground loops or digital noise.

### 1.2 Output

Output is by either OPA458 high power opamps. Output can be up to 1 A continuous (see Figure 3.1), at voltages up to 24 V depending on the power supply, VS.

The board contains space for four output channels allowing for voltages between 0 V and VS. Alternatively the channels can be combined to form two bipolar output channels, permitting outputs up to ±VS. See Section 2 for details. Note that these are not rail-to-rail opamps: the minimum possible output is around 300 mV, so applications that require lower voltages than these must use the bipolar configuration.

### 1.3 Input

Error signal acquisition is done by taking a balanced measurement between a thermistor and a set resistor. The board produces an excitation voltage, usually 1.0 V, and measures the difference in current between the thermistor and resistor to produce a temperature measurement. For less demanding applications the set resistor can be on-board. For the highest stability, the precision resistor should be placed next to its paired thermistor.

This measurement is performed by an INA330 chip, of which there are two present on the board. The entire analogue section is electrically isolated from the rest of the board to prevent noise on the electrical ground affecting the measurement.

There are therefore two possible input channels by balanced thermistor measurements. See Section 2 for details.

### 1.4 Commands

Control of the device is via serial connection over USB. It accepts commands, detailed in Appendix A. A Labview interface is also available which handles this communication.

4

## Section 2

# Connector Pins

This section describes the usage and pin-out for all the connectors on the board. See Figure 2.1 for reference as to their locations.

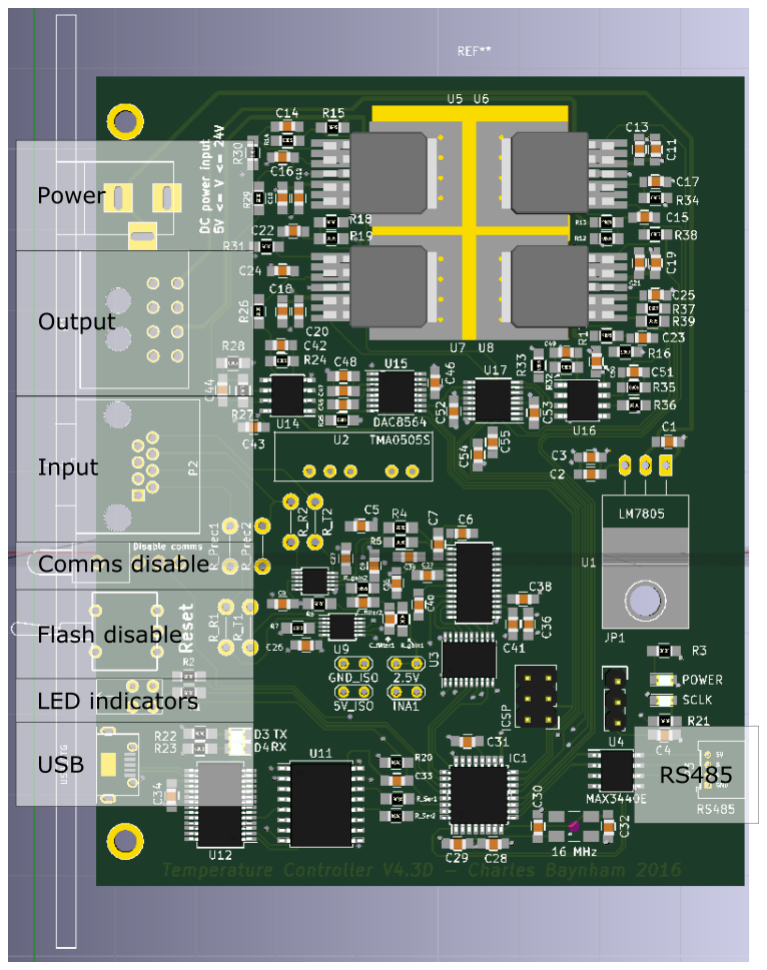
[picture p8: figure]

Figure 2.1: Layout of connectors on the board

5

### 2.1 Power

Power supply is via a standard 2.1 mm, centre-positive barrel connector. The board expects a DC voltage up to 30 V and of at least 7 V, limited by the LM7805 power regulator that powers most of the electronics. Whatever voltage is supplied here will be the maximum possible output control voltage. When choosing what voltage to supply, the user should take note of considerations in Section 3.1 regarding opamp overheating.

### 2.2 Output

Pin Purpose
1 | GND
2 | GND
3 | GND
4 | GND
5 | Unipolar output 1 or bipolar 1 positive output (BPA)
6 | Unipolar output 2 or bipolar 1 negative output (BPA)
7 | Unipolar output 3 or bipolar 2 positive output (BPB)
8 | Unipolar output 4 or bipolar 2 negative output (BPB)

Table 2.1: Pin connections for the output

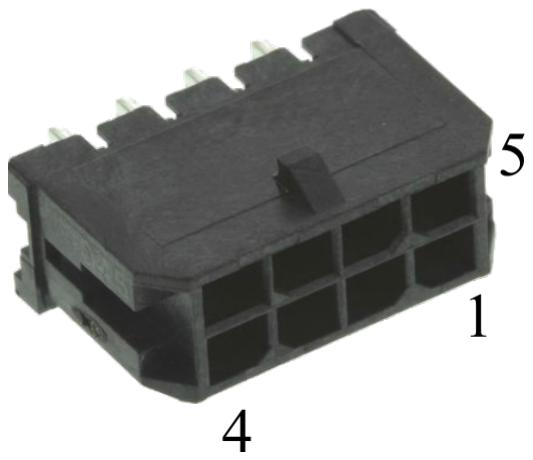
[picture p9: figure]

Figure 2.2: Molex MICRO
FIT 3.0 series 43045 output connector

The output connector is a Molex MICRO FIT 3.0 series 43045. It has 8 contacts, 4 of which are the OPA outputs and 4 are GND. In unipolar operation the device to be controlled (hereafter the plant) should be connected to one of the channels and GND. For bipolar operation connect to both the OPA output channels and leave the GND pins unconnected.

6

### 2.3 Thermistor input

Pin Common colour Purpose
1 Orange and white GND
2 Orange | Set resistor 1 +
3 Green and white | GND
4 Blue | Thermistor 1 +
5 Blue and white | GND
6 Green | Set resistor 2 +
7 Brown and white | GND
8 Brown | Thermistor 2 +

Table 2.2: Pin connections for the error signal input

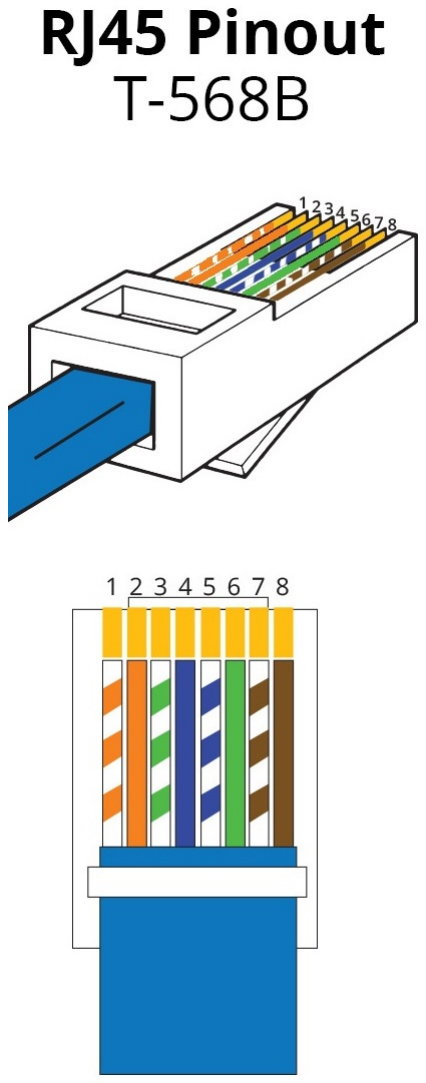
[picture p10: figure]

Figure 2.3: Pinout for a
RJ45 T568-B connector 2

The error signal is produced by an INA330 chip that places a 1.0 V excitation voltage (Vexcite) across both a thermistor (Rtherm) and a set resistor (Rset) and measures the difference in current. The signals in the RJ45 connector should therefore be connected to a thermistor and the set resistor. If an on-board set resistor is in use (see Section 3.4) then the setpoint resistor pin on the input connector should be left floating.

The RJ45 connector accepts standard Ethernet-style cat5 cable. This contains 4 twisted pairs, each of which is assigned to a channel. Table 2.2 assumes the standard T568-B colour scheme for RJ45 mounted CAT5 cable (orange, blue, green, brown: solid and dotted).

2
Image from http://blog.showmecables.com/rj45-pinout/

7

### 2.4 Switches

There are two switches present on the board:

The vertical switch, COMMS DISABLE can be used to disable / enable updating of the controller via USB connection. When this is set to disabled, all functions that alter the state of the controller will be prohibited (monitoring commands still work). When set to enabled, the controller functions as normal. This is intended to prevent accidental pertubation of a system under control.

The horizontal, momentary switch RESET causes a complete system reset.³

### 2.5 LEDs

The two front-mounted LEDs indicate the status of the lock(s) in progress. The LEDs are unlit if the device is currently outputting a constant voltage. If attempting to perform a lock, the two LEDs display the current distance from the setpoint of the lock controlling their respective control channels. A solid light means that the error signal is less than 0.01 V, a slow flash means between 0.01 V and 0.1 V and a quick flash means greater than 0.1 V. These threshold values are defaults but can be altered over the serial connection (see Appendix A for a full listing of available commands).

Locks are indexed as follows:

LED | Output channel
1 | 1
| 2 BPA
2 | 3
| 4 BPB

Table 2.3: LED assignments

3Pressing this switch is actually not strictly equivalent to a power cycle as it does not reset the ADC. However, in the initial setup section of the software the ADS is reset via its SPI interface, so these two methods should give identical results.

8

### 2.6 USB

The USB interface takes a micro-USB cable, allowing for monitoring and control over the system. The interface is isolated from the rest of the board to prevent ground loops.

Communications are handled by a FTDI USB - serial interface IC which presents itself as a virtual COM port. Communication is then done via serial commands at a baud rate of 57600. See Appendix A for more info on commands accepted.

9

## Section 3

# Options and Hardware Configuration

There are various points at which the board can be customised for a particular use case. Each section indicates default choices that will result in sensible behavior and are pre-installed on the boards.

The file Pins.h contains the descriptions of these customizations. If changes are made to the default settings, the user must alter this file and re-flash the device to reflect the changes, as described in Section 3.6.

### 3.1 OPA Choice

The four channel version of this temperature controller only has the option for output via OPA548. These are compact devices, heatsunk to the ground plane and capable of monitoring for thermal overload and accurately limiting current down to 0 A.

Figure 3.1 shows the output currents that these devices are capable of. The power dissipated by the OPAs depends on the difference between the voltage supply and the operational voltage. For example, if the supply voltage is 15 V and 5 V of output is requested, the OPAs will have to dissipate a 10 V voltage drop across them. Depending on the current supplied, this can result in a considerable power.

The power supply voltage and opamp family should therefore be chosen bearing in mind the intended output voltage and current of the device, with reference to Figure 3.1.

10

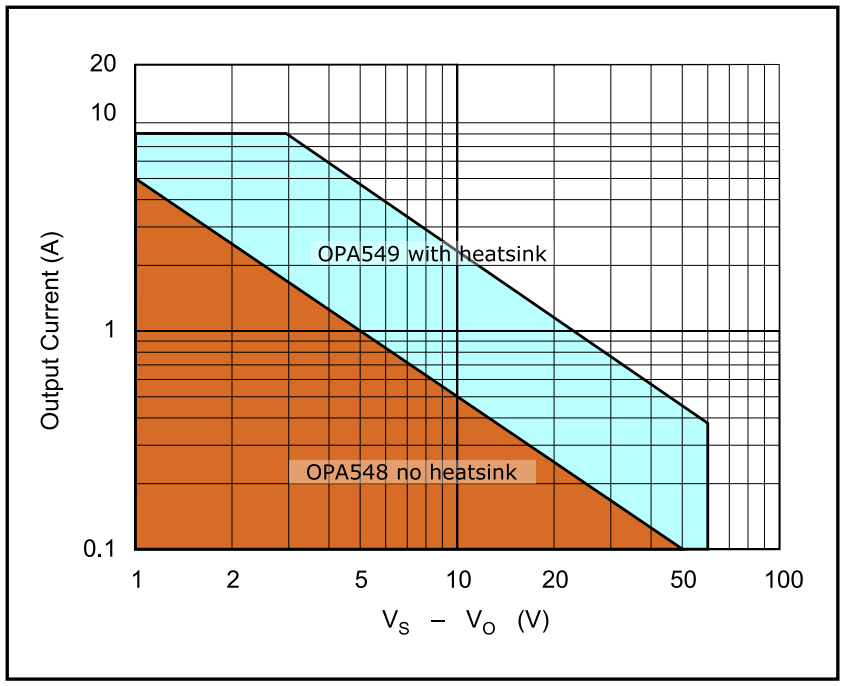
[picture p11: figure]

Figure 3.1: Safe Operating Area (SOA) for the OPA devices. VS and VO are the supply voltage and output voltage respectively. For the OPA549, this assumes the use of the heat-sink recommended. Diagram adapted from the OPA548 and OPA549 data-sheets. The OPA549 is not available with the 4 channel board option.

### 3.2 OPA gain

The DAC outputs voltages ranging from 0 V to 2.5 V. These are amplified by the OPA opamps to reach the desired output voltages. The choice of gain resistors R12 to R19 set the gain of this amplification and therefore the maximum possible output voltage using the formula:

G =

Rx + Ry
Rx

=⇒ Vmax =

Rx + Ry
Rx
× 2.5 V | (3.1)

Default: 100 kΩ and 500 kΩ, gain = 6x, Vmax = 15 V

### 3.3 Instrumentation gain

The input current sensing chips work by current through a gain resistor to match the current difference between the thermistor and set resistor they are measuring, as de-

11 scribed in Section 6.3. The choice of resistors Rgain1 and Rgain2 therefore set the range of inputs that are available.

For precise sensing near the setpoint, a large gain should be chosen. However, in order to make possible a wide range of inputs, a smaller gain is appropriate. If you choose to alter the default gains, you must ensure that both Rgain1 and Rgain2 are the same and their values are updated in Pins.h (see Section 3.6).

Default: 51 kΩ giving a 7

◦C to 36 ◦C temperature sensing range

### 3.4 Setpoint resistors

For applications that do not require extreme stability, it is possible to place the set resistor on the board in footprints Rprec1 and Rprec2. If this is done, the external precision resistor connections should not be made.

Although it is possible to lock to arbitrary resistance values, various advantages are gained by operating at the point where Rthermistor = Rset. In particular, operating at this point means that noise in the voltage reference or EMF noise from other sources will not affect the setpoint. Also, for small values of Vout the device will increase the gain of the input stage of the ADC, allowing greater sensitivity.

Again, for less demanding applications this is unnecessary: on-board precision resistors and digitally defined setpoints will provide sufficient resolution.

Default: 10 kΩ on-board resistors

### 3.5 Sensing series resistors

Unfortunately, the INA330 instrumentation amplifiers struggle to drive even modest capacitive loads, such as that presented by 30 cm of BNC cable. For this reason a 1 kΩ resistor is necessary in series with the thermistor and precision resistor to prevent bias voltage oscillations.

For the most demanding applications this series resistor can be removed and replaced with a piece of wire, reducing sensitivity to board temperature but necessitating short wires to the thermistor / set resistor.

Default: 1 kΩ precision resistor

12

### 3.6 Pins.h

Once customisation options have been chosen, the user must re-flash the device with a version of the source code reflecting these choices. To do this, the file Pins.h should be updated with the changes made and then the software should be compiled and uploaded using e.g. the Arduino IDE. Remember to temporarily re-enable flashing by using the vertical switch on the front panel.

13

## Section 4

# Initial setup

The procedure for setting up a board is therefore as follows:

1. Optional: Choose what configuration you require in accordance with Section 3, or accept the defaults.
2. Optional: If you chose to customize your board in the previous step, make these modifications now.
3. Optional: Open the Pins.h file in the MC software folder. Edit it in accordance with your choices or leave it at defaults. (See the Doxygen documentation (Appendix B) for an in-depth description of each option)
4. Solder the OPA drivers you chose to the board if using the single channel board. The dual channel board comes pre-populated.
5. Using Atmel Studio and an AVRISP mkII programmer, connect to the ISCP header on the board and upload the Optiboot boot-loader file ./CodeforMicrocontroller/ optiboot_xplained328p.hex. This step only has to be performed once per microprocessor.
The board must be powered via the barrel-jack connector during this step.
6. Using the Arduino IDE, compile and upload the code to the device. After this is done, remember to re-enable flashing using the FLASH DISABLE jumper.

After this process is complete, the device will appear over USB as a COM port. In order to test that everything went well, send the command *TST (at baud rate 57600). If the response “OK” is received, the software is installed correctly and communication between the microprocessor and the ADC is working.

14

## Section 5

# Voltage Conversion Formulae

The readings output by the device will be in volts, whereas usually the user will be interested in determining the resistance of a thermistor. For more details about how this voltage is produced, see Section 6.3. The voltage output Vout is the voltage produced by the INA330 instrumentation amplifier according to its gain resistor Rgain1 or Rgain2. To convert this to a resistance, you must know the resistance of the set resistor (default Rset = 10 kΩ), the excitation voltage (Vexcite = 1.0 V), the gain resistance (Rgain = 51 kΩ) and the series resistance (default Rseries = 1 kΩ). Use the following formulae:

Rtherm =

1

Rset + Rseries

−

Vout

Vexcite.Rgain −1
− Rseries | (5.1)

or

Vout = VexciteRgain
1

Rset + Rseries

−

1

Rtherm + Rseries
(5.2)

Thus, close to the set point, i.e. for small values of Vout, Vout is linearly related to resistance.

15

## Section 6

# Hardware Design

The board is designed to be rack-mounted with dimensions of 100 mm × 80 mm. It is compatible with IEC 60297-3/-4 specs regarding dimensions and can fit front panels such as e.g. RS 258-2920.

### 6.1 Isolation

Since the error signals read by this board are at DC, much care was taken to avoid ground loops and crosstalk that could introduce bias. The ADC described in Section 6.2 implements various filtering methods, but the board is also designed to prevent extraneous noise.

The USB input interface is opto-isolated from the rest of the board, with power for the FTDI USB chip provided by the computer host. Also the entire analog section; incorporating the ADC, instrumentation amplifiers and input opamps; is isolated from the rest of the board and powered by a DC-DC converter.

Although the output stages are not isolated from the rest of the board due to their high power requirements, care has been taken to manage high frequency digital return current in order to avoid signal crosstalk. The board has internal ground and power planes to reduce EMI and these both contain a bottleneck at the DAC: the point at which digital signals end and analog signals begin. This design is intended to keep digital return currents within the digital section of the board, avoiding pollution of the output stages.

16

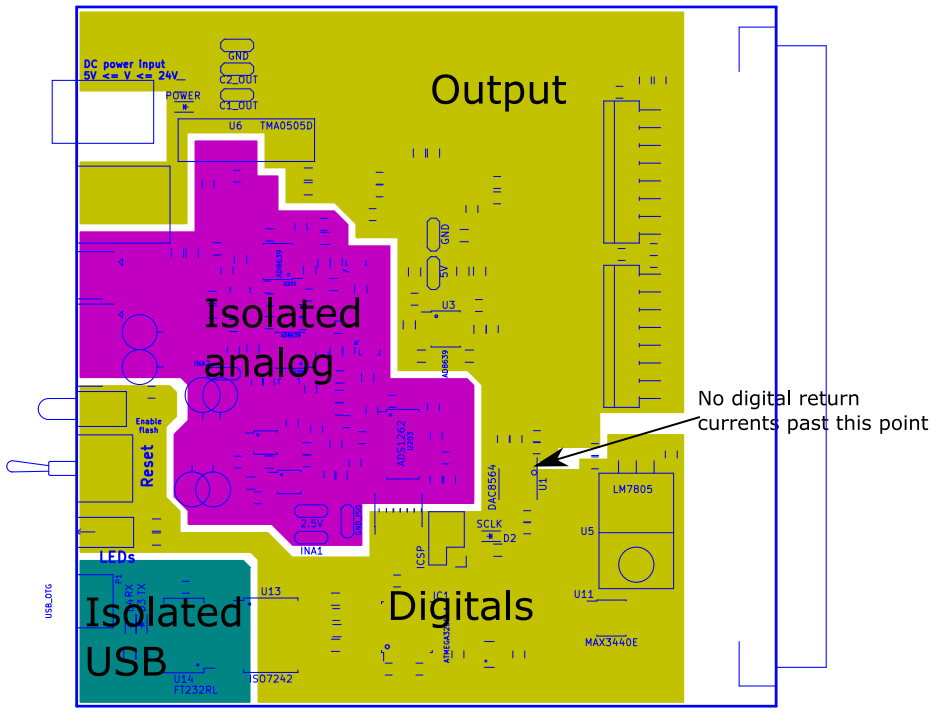
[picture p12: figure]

Figure 6.1: Segmentation of the 2 channel board for isolation and ground loop considerations. 4 channel board is similar

### 6.2 ADS1262 - Analog to Digital Converter

The ADS1262 is a nominal 32-bit ADC produced by Texas Instruments. During a temperature reading it is configured to use a two stage digital filter. The first order provides a fixed 5th order sinc filter. The second stage is a programmable order sinc filter, set to 4th order. These two together result in an 0.58 Hz −3 dB bandwidth, with poles at 50 Hz. On top of this, a simple analog external RC low-pass filter prevents aliasing.

The ADS1262 has inherently low input offset bias however, to combat any residual bias, every measurement is taken twice with the input signal paths swapped over via the internal analog MUX.

The IC also contains an optional Programmable Gain Amplifier (PGA) stage. The micro controller monitors the signals it reads and, if it detects several measurements in a row that would have benefited from increased gain, it automatically boosts the gain stage to increase sensitivity further. If the signal later becomes too large for the gain selected this is also automatically detected and corrected by the micro controller.

17

Because of this re-sampling and filtering, a single measurement can take up to 5 s to complete. Programs that interface with the temperature controller should therefore be aware that commands such as ERRO? 1t can take up to 5 s and should take appropriate steps to avoid timeout. The Labview interface handles this automatically.


Figure 6.2: Flow diagram of the ADS1262. Reference: ADS1262 datasheet by Texas Instruments

### 6.3 INA330 - Thermistor Amplifier

The thermistor / setpoint precision resistor comparison is done by an INA330 chip. These chips take a reference voltage, 1.0 V on this board, ratiomatically derived from the stable 2.5 V reference of the ADS1262. This is buffered and used to drive both the thermistor and the resistor. The current difference between these two arms is then forced through a gain resistor, Rgain1 or Rgain2 (by default 51 kΩ), amplifying it with respect to the 2.5 V reference. This signal is then read by the ADC and compared to the 2.5 V reference in differential mode.

Figure 6.3 shows a schematic of the INA’s operation. For a resistance to voltage conversion formula use Equation 5.1.

18

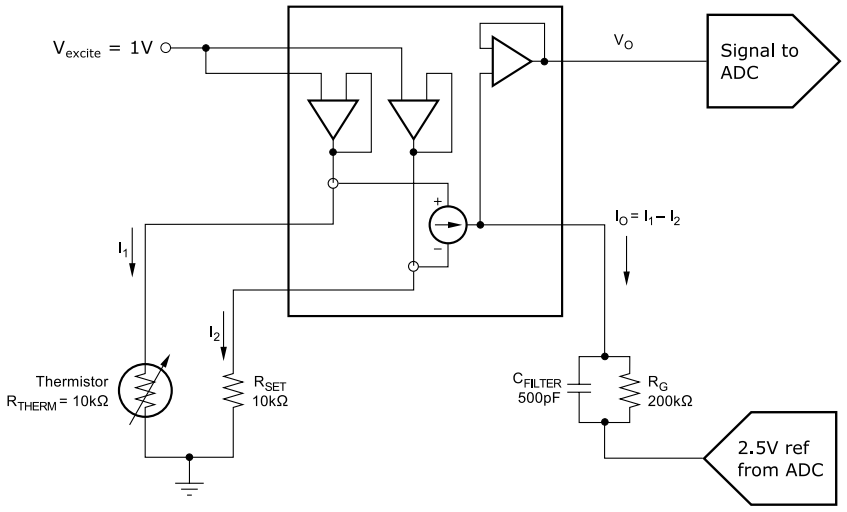
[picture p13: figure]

Figure 6.3: Flow diagram of the INA330. The 2.5 V reference comes from the ADC and the output voltage is refereed to this reference. The 1.0 V excitation reference is derived from the 2.5 V reference ratiomatically for maximum common-mode rejection. Diagram adapted from INA330 datasheet by Texas Instruments.

### 6.4 OPA548/9 - Output Amplifiers

The final output to the plant is handled by an OPA548. These amplify the 0 V → 2.5 V signal produced by the DAC to the voltage required by the user, set by gain resistors as described in Section 3.2.

### 6.5 DAC8564 - Digital to Analog Converter

The production of the analog signal is done by the DAC8564: a 16-bit digital to analog converter, referenced to its own internal 2.5 V reference.

Its output ranges from 0 V to 2.5 V. This signal is then either amplified by the OPAs to become the output level, or doubled by a AD8639 auto-zeroing opamp to control the current limiting feature of the OPAs.

### 6.6 ATMega328p - The micro controller

The brain of the device is an ATMega328p MC. This is the same processor that is found on the Arduino Uno or Nano, and the board is configured (instructions in Section 4) to

19 appear as an Arduino Nano to the computer. However, by breaking the Arduino into pieces several advantages are gained including reduced board space and the option to add on-board isolation to the USB interface.

The ATMega is clocked from a 16 MHz full-swing crystal. When the board is assembled for the first time the ATMega’s flash memory will be blank and the device with not be programmable over the usual USB interface. For the first time only, programming must be done by the ISCP header provided, as described in Section 4.

### 6.7 RS485

The board is equipped with a 4 pin Molex PicoBlade 53048-0410 connector that enables RS485 communications. This is currently unimplemented, but will allow for control of up to 255 RS485 boards from a single USB connection.

20

## Section 7

# Software Structure

The code running on the micro-controller is written in C++. The ATMega328 is set up to appear the same as an Arduino Nano: it is therefore possible to compile and upload the code using the usual Arduino IDE. Note that re-flashing like this this requires two things: a) the FLASH DISABLE switch should be set correctly (see Section 2.4) and b) the boot-loader must have been installed using the ISCP header (see Section 4).

The code-base makes considerable use of the object-orientated programming style. While this can appear daunting at first, in the long run it simplifies modifications and results in more compartmentalized code that is easier to understand. This overview and the more in-depth Doxygen documentation both assume some familiarity with concepts such as virtualisation, inheritance, abstraction and polymorphism.

There are very many online and offline resources that can give you an overview of these ranging from 1 page to multiple-volume books. For a quick starting point, try
https://www.cs.bu.edu/teaching/cpp/inheritance/intro/ and https://www.cs.bu.edu/teaching/cpp/polymorphism/intro/. (https://www.cs.bu.edu/teaching/cpp/polymorphism/intro/)

### 7.1 Doxygen

The code is thoroughly commented throughout to aid comprehension. These comments have been written to comply with the requirements of the documentation program Doxygen http://www.stack.nl/~dimitri/doxygen/. It is therefore simple to compile all these comments into a manual by installing the Doxygen program on your computer, launching the wizard, selecting the Doxyfile file in the temperature controller’s source code and running the wizard. This will produce a neatly linked set of HTML files that can be opened in any browser. It will also produce LATEX output, the result of which is appended to this document in Appendix B.

21

The Doxygen output is detailed and should be considered the authority if modification to the code is required, but this section provides an overview of the code structure.

### 7.2 Code Overview

As per usual object-orientated design, the jobs performed by the temperature controller are split between objects. Two of the most important are ErrorChannels and CtrlChannels. These classes manage interactions with the world. They are abstract classes, and provide a template of functions which must be fulfilled by their derived classes.

For instance, CtrlChannels have a method setCtrl() which sets the output voltage available at the OPA. This method takes a double as a parameter, the new control level, which adheres to a convention used throughout the code: all error readings or control outputs are given as a number between -1 and +1 where -1 corresponds to the lowest possible level and +1 corresponds to the highest.

A specialisation of CtrlChannel is V4 OPA OutputChannel. This overrides the “pure virtual” methods in CtrlChannel and writes a voltage to the output channel it manages. On initialisation this object is assigned to one of the OPAs. A value of for output -1 would correspond to 0V, a value of +1 would be +MAX VOLTAGE V.

A different specialisation of CtrlChannel is V4 OPA OutputChannelBipolar. This object also performs output, but rather than outputting a voltage on a single OPA, it uses 2 OPAs at the same time in order to output a bipolar differential level.

ErrorChannels have similar functionality but are used for input instead of output. However, since taking a reading can take several seconds (see Section 6.2) there is a bit more structure involved. Readings are initiated with startReading(). Before this happens, the calling code should check that no reading is already in progress by calling globalReadInProgress(). Once a reading has been started, its progress can be checked by calling readingReady() and then its result can be output using getReading().

Other important objects in the code are:

Controllers Contain references to an ErrorChannel, a CtrlChannel and an Algorithm. Every time doLoop() is called, attempt to take a reading from the ErrorChannel, process it with the Algorithm and output it with the CtrlChannel.

Algorithms An abstract class that defines an object responsible for processing an input error signal and returning the new control level. This object should contain information about the set-point and any limits applied. An example implementation is PIDAlgorithm.

22

CommandHandler An independent object that can be included as an Arduino library in any project. This object manages the input and parsing of serial commands. It uses a hashing algorithm to minimize memory consumption and assigns all memory on the stack to avoid fragmentation. It is responsible for calling the appropriate function when a command is issued. See its own Doxygen documentation for much more detail.

A typical cycle in the code looks like this:

1. Check CommandHandler for new commands and execute them if present.
2. For all Controllers, see if a lock is in progress
3. If so:

If an ADC reading is in progress do nothing.
If no reading is in progress, start one.
If an ADC reading for this channel is complete, get the result and move to
step 4.
4. Feed the result of the reading into the contained Algorithm
5. Get the new control level back from the Algorithm and pass this to a CtrlChannel for output.

23

# Appendices

24

## Appendix A

# Available Commands

The commands recognised by the controller are defined in the file ./Code_for_microcontroller/ YbTempCtrl/CommandDefinitions.h and the Doxygen documentation (Appendix B) for
this file contains a complete list of them.

This documentation is reproduced here for convenience. The following is automatically generated from the code’s markup, so please excuse any odd formatting. All parameters should be separated by spaces. All commands must be followed by a newline (ASCII 10) character.

A.0.1 CommandDefinitions.h File Reference

Defines all the commands that the device listens for.

#include "CommandHandler\CommandHandler.h"

Functions

template<size t size>
CommandHandlerReturn registerCommands (CommandHandler< size > ∗h)

Register the commands.

25

Detailed Description

Defines all the commands that the device listens for.

This file contains definitions of all the commands that can be issued to the device.

Command processing is done via the CommandHandler class which has its own documentation.

All functions to be called by CommandHandler take exactly the same form: they return void and take a const ParameterLookup object as an argument. This object dispenses c strings as the params, e.g. params[1] is the first parameter, etc. (params[0] is the command itself). See the definition of #commandFunction for the required spec.

All commands are parsed and stored using a hash function for memory efficiency, and are case-insensitive.

The following is a summary of the available commands. If query form of a command with different functionality exists is it listed separately. If it's identical, this is shown as e.g. ∗TST(?). If no query / non-query form exists, it is not shown in this table; calling it will result in an error.

Command | Description | Params | Output
∗TST | Test comms | 0 | ”Loud and clear!”
∗TST? | Test comms | 0 | ”Query received”
∗IDN(?) | Identify | 0 | ”ARDUINO PID”
∗VER(?) | Output version string | 0 | e.g. ”v4.1”
∗GIT(?) | Output git version string | 0 | e.g. ”5a21cb0”
∗RST | Reset the device (N.B. does not clear EEPROM) | 0 | -
∗DFU | Puts the device into DFU mode (does 10x resets, expecting code upload) | 0 | -
STOR | Store a command in EEPROM to be exe-cuted on startup | ”command to be called on startup” | ”Done”
| | Multiple commands can be stored by sep-arating them with a ';' | ”#StoreCommand error: command too long”

26

Command | Description | Params | Output
APPE | Append a command to EEPROM to be executed on startup | ”command to be called on startup” | ”Done”
| | Multiple commands can be stored by sep-arating them with a ';' | ”#StoreCommand error: command too long”
RETR | Retrieve any stored commands from EEPROM | 0 | Stored command or ”None”
WIPE | Erase any stored commands in EEP-ROM | 0 | ”Done”
ERRO(?) | Query the error sig-nal on given channel. | [channel = 1t,2t,1v,2v] for signals 1 or 2 from thermistor input or voltage input | Error signal float
| | | If thermistor read-ing, voltage read from -2.5 -] +2.5
| If this channel is be-ing controlled, return the previously mea-sured value. Else, measure it now and then return. | | If voltage reading, re-turn voltage from -5 -] +5 V
| | | e.g. ”-0.00151”
STAT(?) | Return a string de-scribing the status of the controller | 0 | t.b.c.
CONT | Set the control signal. | [output channel = 1, 2, 3, 4, BPA, BPB] [voltage = 0 - max for single, -max - +max for BP] | e.g. ”#SetControl BP 2.500”

27

Command | Description | Params | Output
| N.B. If this is called during a lock this will set the control sig-nal to the given value, but this may subse-quently be changed by the locking algo-rithm
CONT? | Query the control sig-nal | [output channel = 1, 2, 3, 4, BPA, BPB] | e.g. ”2.500”
THER? | Check the thermal state of the given channel. For the bipolar channel, re-turn ”BAD” if either OPA is overheated | [output channel = 1, 2, 3, 4, BPA, BPB] | e.g. ”GOOD” / ”BAD”
LIMI | Set software limits on the output voltage | [output channel = 1, 2, 3, 4, BPA, BPB] | e.g. ”#SetLimits 1 0.000 3.000”
| | [min voltage]
| | [max voltage]
LIMI? | Query limits | [output channel = 1, 2, 3, 4, BPA, BPB] | e.g. ”0.000 3.000”
THRE | Set thresholds at which the LEDs will start flashing. | [thresholdHigh] [thresholdLow] | e.g. ”#setThresholds 0.1 0.01”
| LEDs will flash fast when the absolute error signal is ] thresholdHigh, slow when it's between thresholdHigh and thresholdLow and light solidly when it's [ thresholdLow
THRE? | Query current LED thresholds | 0 | e.g. ”0.1, 0.01”
CURR | Set hardware limits on the output current | [output channel = 1, 2, 3, 4, BPA, BPB] | e.g. ”#SetCur-rentLimit 1 1.000”
| | [max current in amps]

28

Command | Description | Params | Output
CURR? | Get current hardware on output current | [output channel = 1, 2, 3, 4, BPA, BPB] | e.g. ”1.000”
SETP | Set setpoint for lock | [output channel = 1, 2, 3, 4, BPA, BPB] | If no lock running on this channel: ”#Set-Setpoint error: no lock running on chan-nel xxx”
| | | Else, e.g. ”#SetSet-point 1 0.000”
SETP? | Query lock setpoint | [output channel = 1, 2, 3, 4, BPA, BPB] | If no lock running on this channel: ”#Set-Setpoint error: no lock running on chan-nel xxx”
| | | Else, e.g. ”0.000”
LOCK | Start PID lock | [input channel = 1t,2t,1v,2v] | e.g. ”#StartLock 1t BP 0.000 1 0.5 0 10”
| | [output channel = 1, 2, 3, 4, BPA, BPB]
| | [setpoint]
| | [Kp] [Ki] [Kd] [N=10]
VOLT | Output a constant voltage | [output channel = 1, 2, 3, 4, BPA, BPB] [voltage = 0 - max for single, -max - +max for BP] | e.g. ”#ConstVoltage 1 2.500”
| N.B. Unlike ”CONT”, this function will output a constant voltage, disabling any PID lock that was previ-ously running on this output channel

Function Documentation

29 registerCommands() template<size t size>

CommandHandlerReturn registerCommands (CommandHandler< size > ∗ h )

Register the commands.

Register the commandFunction functions with the CommandHandler object, defining:

The command used to call them

The number of parameters they must be called with

Parameters

h Pointer to a CommandHandler object

Template Parameters

size Number of commands this CommandHandler can contain. This will be inferred by the number specified in its definition.

Returns

A CommandHandlerReturn enum detailing any errors that occured during the execution of this method.

30

## Appendix B

# Full Doxygen documentation

The following pages are the full documentation of the code, produced automatically by Doxygen. Doxygen is a code commenting system that allows you to write structured comments throughout your code which can later be extracted into a code reference.

To get the latest version of this reference, incorporating any changes, you need to install Doxygen, run the Doxywizard, load the file ./Code_for_microcontroller/ YbTempCtrl/Doxyfile and click “Run doxygen”. This will produce HTML and LATEX output.

It will also generate a file called make.bat in ./Code_for_microcontroller/YbTempCtrl/
doc/latex/make.bat. Execute this file to produce the updated LATEX code reference.
To incorporate this into the manual you are currently reading, just recompile the latex
from ./Manual/TemperatureControllerManual.tex.

31

## Yb Temperature Controller

### Generated by Doxygen 1.8.14

CONTENTS | i

## Contents

1 Yb+ temperature controller | 1
1.1 Introduction | | 1
1.2 Documentation | | 2
1.3 Version Control | | 2
1.4 Available commands | | 2
1.5 Code outline | | 3
2 arduino-pin-toggler | 3
2.1 Introduction | | 3
2.2 Usage | | 3
3 Todo List | 4
4 Module Index | 4
4.1 Modules | | 4
5 Namespace Index | 4
5.1 Namespace List | | 4
6 Hierarchical Index | 5
6.1 Class Hierarchy | | 5
7 Class Index | 5
7.1 Class List | | 5
8 File Index | 6
8.1 File List | | 6
9 Module Documentation | 7
9.1 Algorithms | | 7
9.1.1 Detailed Description | | 7
9.2 Control signal output | | 8
9.2.1 Detailed Description | | 8
9.3 Error signal input | | 9
9.3.1 Detailed Description | | 9

Generated by Doxygen

ii | CONTENTS
10 Namespace Documentation | 10
10.1 YbCtrl Namespace Reference | 10
10.1.1 Detailed Description | 10
10.1.2 Enumeration Type Documentation | 11
11 Class Documentation | 11
11.1 YbCtrl::Algorithm Class Reference | 11
11.1.1 Detailed Description | 12
11.1.2 Member Function Documentation | 12
11.2 YbCtrl::Controller Class Reference | 15
11.2.1 Detailed Description | 16
11.2.2 Constructor & Destructor Documentation | 16
11.2.3 Member Function Documentation | 17
11.3 YbCtrl::CtrlChannel Class Reference | 20
11.3.1 Detailed Description | 21
11.3.2 Member Function Documentation | 21
11.4 YbCtrl::ErrorChannel Class Reference | 26
11.4.1 Detailed Description | 27
11.4.2 Member Function Documentation | 27
11.5 YbCtrl::PIDAlgorithm Class Reference | 31
11.5.1 Detailed Description | 32
11.5.2 Constructor & Destructor Documentation | 32
11.5.3 Member Function Documentation | 33
11.6 pinToggler< numPins > Class Template Reference | 36
11.6.1 Detailed Description | 36
11.6.2 Member Function Documentation | 37
11.7 YbCtrl::TemporaryLooper Class Reference | 38
11.7.1 Detailed Description | 39
11.8 YbCtrl::V4_ADC_ChannelPair Class Reference | 39
11.8.1 Detailed Description | 40
11.8.2 Constructor & Destructor Documentation | 40
11.8.3 Member Function Documentation | 40
11.8.4 Member Data Documentation | 44
11.9 YbCtrl::V4_OPA_OutputChannel Class Reference | 45
11.9.1 Detailed Description | 46
11.9.2 Constructor & Destructor Documentation | 46
11.9.3 Member Function Documentation | 46
11.10YbCtrl::V4_OPA_OutputChannelBipolar Class Reference | 52
11.10.1 Detailed Description | 53
11.10.2 Member Function Documentation | 53

1 Yb+ temperature controller | 1
12 File Documentation | 58
12.1 arduino-pin-toggler/pinToggler.h File Reference | 58
12.1.1 Detailed Description | 59
12.1.2 Macro Definition Documentation | 59
12.1.3 Enumeration Type Documentation | 59
12.2 CommandDefinitions.h File Reference | 60
12.2.1 Detailed Description | 60
12.2.2 Function Documentation | 62
12.3 CommandHandler/CommandHandler.h File Reference | 63
12.3.1 Detailed Description | 63
12.4 Pins.h File Reference | 63
12.4.1 Detailed Description | 63
12.5 Pins_2chan.h File Reference | 63
12.5.1 Detailed Description | 64
12.5.2 Variable Documentation | 65
12.6 Pins_4chan.h File Reference | 69
12.6.1 Detailed Description | 70
12.6.2 Variable Documentation | 70
Index | 75

## 1 Yb+ temperature controller

### 1.1 Introduction

This is the source code for the Yb+ temperature controller, programmed and designed by Charles Baynham.

It is intended for high precision control of cavities, however can be used to control laser diode temperature or other low-bandwidth lock processes that could benefit from digital control. Error signal input can be either by voltage (from -5V to +5V) or through a balanced thermistor reading, mediated by a built-in INA330 IC. For demanding temperature applications, the latter method is recommended.

This code is designed to be uploaded to an ATMega328 microprocessor. It is written in C++ and can be compiled and uploaded via the Arduino IDE. However, if you intend to work on it for any significant length of time, I highly recommend that you install a more capable IDE. I wrote this software in Visual Studio Community which is a free download from Microsoft and will make your life so much easier.

### 2 CONTENTS

### 1.2 Documentation

If you are reading these comments in a pdf or html format then you are currently looking at the compiled documentation. If, however, you are reading this README.md file in a text editor then your first step before editing the code should be to get hold of the full code documentation.

The code is documented throughout using the Doxygen commenting system. These can be compiled easily into a pdf or a local html website by:

1. Installing Doxygen from http://www.stack.nl/∼dimitri/doxygen/download.html
2. Using the Doxygen GUI to load the file in this folder, Doxyfile
3. Selecting Run doxygen on the Run tab.

This will produce the html documentation and, if you have pdflatex installed, source files for a pdf.

Alternativly, open the Documentation.pdf file that should be bundled with this repo.

### 1.3 Version Control

This folder is a GIT repository that maintains a full history of development including every change since this code was started. This history is contained in a hidden folder called .git which should not be accessed directly.

The upshot of this is that the code you see may not be the latest, and may instead be a "snapshot" of a previous state. To ensure you are looking at the latest iteration, and to make updates, install a git client of your choosing. https://windows.github.com/ is very lightweight, http://www.sourcetreeapp.com/ is more fully featured and https://desktop.github.com/ strikes a balance between the two.
Once installed, "checkout" the master branch for the latest code version. See http://rogerdudler.←-github.io/git-guide/ for a simple guide.

Note that this code makes use of several submodules. If you "clone" the code, you will by default not get these. In order to correctly get the code for these as well, run the command git submodule update --init --recursive after cloning the main code. If you use a more advanced GUI such as SourceTree then this should be handled for you automatically.

### 1.4 Available commands

The device listens for commands on a virtual serial COM port served via USB. The USB connection is electrically isolated to avoid ground pollution.

Baud rate should be set to 57600.

The board also contains footprints to enable RS485 communication via a backplane connection, however this is not yet implemented.

For a detailed description of all the commands available, see the documentation for CommandDefinitions.h.

1.5 Code outline | 3

### 1.5 Code outline

This code is split into classes according to the object orientated paradigm. A typical lock could be implemented as follows:

1. Define a YbCtrl::ErrorChannel object (or rather, an implementation of YbCtrl::ErrorChannel) to handle input.
2. Define a YbCtrl::CtrlChannel object to handle output
3. Define a YbCtrl::Algorithm object to implement the locking transfer function required.
4. Pass these three objects to a new YbCtrl::Controller object.
5. Loop, calling YbCtrl::Controller::doLoop() on each iteration.

For more detail, every class and method is individually documented. See the Classes section or the Namespaces section to see more.

Todo Implement RS485 Modbus protocol

Copyright

Charles Baynham 2016

## 2 arduino-pin-toggler

### 2.1 Introduction

This Arduino library manages the toggling of arbitary pins at controllable rates. For example, it can be used to flash an LED at different speeds according to the state of your device.

It works using interrupts and is designed to be lightweight when running, so will not interfere with existing code.

This library requires exclusive usage of TIMER1 so is incompatible with libraries that also use this timer.

### 2.2 Usage

Include the class by adding #include <pinToggler.h> to your sketch. Init the class by passing it an array of pins that will be toggled. E.g.

int pins[3] = {13, A4, A5};
pinToggler<3>::init(pins);

The template parameter (<3> above) defines the total number of pins being controlled.

These pins will start LOW, not toggling.
To start the toggling, set their speed to OFF, SLOW, MEDIUM, FAST or MAX. E.g.

pinToggler<3>::setFlashRate(0, SLOW);

N.B. The template parameter (here <3>) must match the one used in pinToggler::init() or this will throw an error. Also the LED parameter in pinToggler::setFlashRate refers to the pins passed to pinToggler::init(), zero-indexed in the order that they appeared in in the array.

The speeds refer to fractions of the max speed, defined by FLASH_FREQ_HZ.

### 4 CONTENTS

Warning

Note that all the function calls here are static members of the class. Although a class object is created, this happens internally. For memory management purposes, be aware that this class allocates 3 ∗ numPins bytes on the heap. Thus, to avoid memory framentation, pinToggler::init() should be called as early in your code as possible.

Copyright

Charles Baynham 2016

## 3 Todo List

File CommandHandler.h
Write the CommandHandler documentation
File Pins_2chan.h
Add option for user to configure different hardware gains on the two OPAs. File Pins_4chan.h
Add option for user to configure different hardware gains on the two OPAs. page Yb+ temperature controller
Implement RS485 Modbus protocol
Member YbCtrl::CtrlChannelReturn
Change to enum class
Class YbCtrl::TemporaryLooper
This class is currently unused: the code in Controller exists but is commented out. It could be used to implement e.g. an autotuning lock or a relocking routine

## 4 Module Index

### 4.1 Modules

Here is a list of all modules:

Algorithms | 7
Control signal output | 8
Error signal input | 9

## 5 Namespace Index

### 5.1 Namespace List

Here is a list of all documented namespaces with brief descriptions:

6 Hierarchical Index | 5

YbCtrl
Namespace to hold all the temperature controller classes | 10

## 6 Hierarchical Index

### 6.1 Class Hierarchy

This inheritance list is sorted roughly, but not completely, alphabetically:

YbCtrl::Algorithm | 11
YbCtrl::PIDAlgorithm | 31
YbCtrl::Controller | 15
YbCtrl::CtrlChannel | 20
YbCtrl::V4_OPA_OutputChannel | 45
YbCtrl::V4_OPA_OutputChannelBipolar | 52
YbCtrl::ErrorChannel | 26
YbCtrl::V4_ADC_ChannelPair | 39
pinToggler< numPins > | 36
YbCtrl::TemporaryLooper | 38

## 7 Class Index

### 7.1 Class List

Here are the classes, structs, unions and interfaces with brief descriptions:

YbCtrl::Algorithm
Abstract class for algorithms | 11

YbCtrl::Controller
Object to manage the locking loop | 15

YbCtrl::CtrlChannel
Abstract object to allow outputting a control signal | 20

YbCtrl::ErrorChannel
Abstract object to allow measuring an error signal | 26

YbCtrl::PIDAlgorithm
Implementation of an Algorithm to perform a PID lock | 31

pinToggler< numPins >
Class for toggling pins | 36

### 6 CONTENTS

YbCtrl::TemporaryLooper
Temporarily divert the lock, before returning to normal | 38

YbCtrl::V4_ADC_ChannelPair
Implementation of an ErrorChannel for the ADS1262 | 39

YbCtrl::V4_OPA_OutputChannel
Implementation of a CtrlChannel for a single-ended output | 45

YbCtrl::V4_OPA_OutputChannelBipolar
Implementation of a CtrlChannel for a bipolar output | 52

## 8 File Index

### 8.1 File List

Here is a list of all documented files with brief descriptions:

ADS1262_reg.h | ??
Algorithm.h | ??

CommandDefinitions.h
Defines all the commands that the device listens for | 60
Controller.h | ??
CtrlChannel.h | ??
ErrorChannel.h | ??
latest_hash.h | ??
MemoryFree.h | ??
PIDAlgorithm.h | ??

Pins.h
Hardware limits and pins | 63

Pins_2chan.h
Hardware limits and pins | 63

Pins_4chan.h
Hardware limits and pins | 69
TemporaryLooper.h | ??
V4_ADC_ChannelPair.h | ??
V4_OPA_OutputChannel.h | ??
V4_OPA_OutputChannelBipolar.h | ??

arduino-pin-toggler/pinToggler.h
Contains all the code for the arduino-pin-toggler library | 58

CommandHandler/CommandHandler.h
Contains all the code for the Arduino CommandHandler library | 63

9 Module Documentation | 7
CommandHandler/compileTimeCrc32.h | ??
CommandHandler/Microprocessor_Debugging/debugging_disable.h | ??
CommandHandler/Microprocessor_Debugging/debugging_enable.h | ??
CommandHandler/Microprocessor_Debugging/debugging_init.h | ??
Microprocessor_Debugging/debugging_disable.h | ??
Microprocessor_Debugging/debugging_enable.h | ??
Microprocessor_Debugging/debugging_init.h | ??

## 9 Module Documentation

### 9.1 Algorithms

Locking algorithms.

Classes

- class YbCtrl::Algorithm
Abstract class for algorithms.
- class YbCtrl::PIDAlgorithm
Implementation of an Algorithm to perform a PID lock.

### 9.1.1 Detailed Description

Locking algorithms.

The classes in this module are responsible for transforming error signals into control signals. They are based on the template base class Algorithm which defines various methods, most important of which is Algorithm::output(double). This method takes an error signal as a parameter (using the -1 -> +1 format that is universal in this codebase) and outputs a desired control signal (also using the same format).

### 8 CONTENTS

### 9.2 Control signal output

Manage output of a control signal.

Classes

- class YbCtrl::CtrlChannel
Abstract object to allow outputting a control signal.
- class YbCtrl::V4_OPA_OutputChannel Implementation of a CtrlChannel for a single-ended output.
- class YbCtrl::V4_OPA_OutputChannelBipolar Implementation of a CtrlChannel for a bipolar output.

### 9.2.1 Detailed Description

Manage output of a control signal.

The classes in this group are collectivly responsible for managing the output of control signals to the real world. Their template base class is CtrlChannel.

9.3 Error signal input | 9

### 9.3 Error signal input

Manage input of an error signal.

Classes

- class YbCtrl::ErrorChannel
Abstract object to allow measuring an error signal.
- class YbCtrl::V4_ADC_ChannelPair Implementation of an ErrorChannel for the ADS1262.

### 9.3.1 Detailed Description

Manage input of an error signal.

The classes in this group are collectivly responsible for managing the input of error signals from the real world. Their template base class is ErrorChannel.

### 10 CONTENTS

## 10 Namespace Documentation

### 10.1 YbCtrl Namespace Reference

Namespace to hold all the temperature controller classes.

Classes

- class Algorithm
Abstract class for algorithms.
- class Controller
Object to manage the locking loop.
- class CtrlChannel
Abstract object to allow outputting a control signal.
- class ErrorChannel
Abstract object to allow measuring an error signal.
- class PIDAlgorithm
Implementation of an Algorithm to perform a PID lock.
- class TemporaryLooper
Temporarily divert the lock, before returning to normal.
- class V4_ADC_ChannelPair
Implementation of an ErrorChannel for the ADS1262.
- class V4_OPA_OutputChannel
Implementation of a CtrlChannel for a single-ended output.
- class V4_OPA_OutputChannelBipolar Implementation of a CtrlChannel for a bipolar output.

Enumerations

- enum CtrlChannelReturn {
CtrlChannelReturn::NO_ERROR = 0, CtrlChannelReturn::NOT_IMPLEMENTED, CtrlChannelReturn::NO_SUCH_CHANNEL, CtrlChannelReturn::CHANNEL_NOT_MANAGED,
CtrlChannelReturn::INVALID_PARAMETER, CtrlChannelReturn::OUT_OF_MEMORY }
Error codes for CtrlChannel operation.
- enum ErrorChannelReturn {
ErrorChannelReturn::NO_ERROR = 0, ErrorChannelReturn::NOT_IMPLEMENTED, ErrorChannelReturn::WRITING_TO_REG_FAILED, ErrorChannelReturn::TIMEOUT,
ErrorChannelReturn::OUT_OF_RANGE, ErrorChannelReturn::PGA_ERROR, ErrorChannelReturn::NO_SUCH_CHANNEL
}
Error codes for ErrorChannel operation.

### 10.1.1 Detailed Description

Namespace to hold all the temperature controller classes.

All the classes contained in the YbCtrl namespace are involved with the input of error signals, output of control signals or calculation of the appropriate ctrl signal from the corresponding error signal.

11 Class Documentation | 11

### 10.1.2 Enumeration Type Documentation

### 10.1.2.1 CtrlChannelReturn

enum YbCtrl::CtrlChannelReturn [strong]

Error codes for CtrlChannel operation.

Todo Change to enum class

Enumerator
NO_ERROR | No error
NOT_IMPLEMENTED | Feature not implemented by derived class
NO_SUCH_CHANNEL | This channel does not exist
CHANNEL_NOT_MANAGED | This channel has no managing Controller
INVALID_PARAMETER | Parameter passed was invalid
OUT_OF_MEMORY | Out of memory

### 10.1.2.2 ErrorChannelReturn

enum YbCtrl::ErrorChannelReturn [strong]

Error codes for ErrorChannel operation.

Enumerator
NO_ERROR | No error
NOT_IMPLEMENTED | Feature not implemented by derived class
WRITING_TO_REG_FAILED | ADC comms failed
TIMEOUT | Reading timeout
OUT_OF_RANGE | Reading out of PGA range
PGA_ERROR | Undefined PGA error
NO_SUCH_CHANNEL | Channel does not exist

## 11 Class Documentation

### 11.1 YbCtrl::Algorithm Class Reference

Abstract class for algorithms.

#include <Algorithm.h>

### 12 CONTENTS

Inheritance diagram for YbCtrl::Algorithm:

YbCtrl::Algorithm

YbCtrl::PIDAlgorithm

Public Member Functions

- virtual double output (double input)=0 Do the locking calculation.
- virtual char ∗ reportState (char ∗ptr)=0 Report state.
- virtual void setOutput (double output)=0 Sets the output.
- virtual void setSetpoint (double setpoint)=0 Sets the setpoint.
- virtual double getSetpoint ()=0
Gets the setpoint.
- virtual void setLimits (double min, double max)=0 Sets output limits.
- virtual bool lockingAlgo ()
Does this algorithm lock?
- virtual operator bool ()
Is this algorithm valid?

### 11.1.1 Detailed Description

Abstract class for algorithms.

This abstract class defines a template for a lock algorithm. The main method is output() which is responsible for taking an error signal and calculating a subsequent output from it. output() obeys the convention followed everywhere in this code that both input and output signals can range from -1 to +1.

As with all abstract classes, the pure virtual methods in this class MUST be overridden by derived classes. The virtual methods SHOULD be overridden.

For an example implementation, see PIDAlgorithm.

### 11.1.2 Member Function Documentation

11.1 YbCtrl::Algorithm Class Reference | 13

### 11.1.2.1 getSetpoint()

virtual double YbCtrl::Algorithm::getSetpoint ( ) [pure virtual]

Gets the setpoint.

Returns
The current setpoint.

Implemented in YbCtrl::PIDAlgorithm.

### 11.1.2.2 lockingAlgo()

virtual bool YbCtrl::Algorithm::lockingAlgo ( ) [inline], [virtual]

Does this algorithm lock?

Returns a boolean describing whether this Algorithm implementation locks or not. E.g. the PIDAlgorithm, a derived implementation of this class, does lock so it overrides this method with

return true;

Currently there are no examples of Algorithms that do not lock.

Returns
true / false

Reimplemented in YbCtrl::PIDAlgorithm.

### 11.1.2.3 operator bool()

virtual YbCtrl::Algorithm::operator bool ( ) [inline], [explicit], [virtual]

Is this algorithm valid?

Return true if this Algorithm is valid for use in calculations. E.g. see PIDAlgorithm for an example of why this may be useful.

Reimplemented in YbCtrl::PIDAlgorithm.

### 11.1.2.4 output()

virtual double YbCtrl::Algorithm::output ( double input ) [pure virtual]

Do the locking calculation.

### 14 CONTENTS

Parameters
in | input | The error signal, ranging from -1 to +1

Returns
The new ctrl level, ranging from -1 to +1

Implemented in YbCtrl::PIDAlgorithm.

### 11.1.2.5 reportState()

virtual char∗ YbCtrl::Algorithm::reportState ( char ∗ ptr ) [pure virtual]

Report state.

Send a string that identifies the currently running algorithm.

Parameters
out | ptr | A buffer to contain the output. Should be at least 128 chars long.

Returns
Returns ptr

Implemented in YbCtrl::PIDAlgorithm.

### 11.1.2.6 setLimits()

virtual void YbCtrl::Algorithm::setLimits ( double min,
double max ) [pure virtual]

Sets output limits.

Set limits on the algorithm's output. Values are from -1 to +1.

Parameters
in | min | The new minimum
in | max | The new maximum

Implemented in YbCtrl::PIDAlgorithm.

11.2 YbCtrl::Controller Class Reference | 15

### 11.1.2.7 setOutput()

virtual void YbCtrl::Algorithm::setOutput ( double output ) [pure virtual]

Sets the output.

Set the output to a specified level, smoothly if possible.

Parameters
in | output | The new output, from -1 to +1.

Implemented in YbCtrl::PIDAlgorithm.

### 11.1.2.8 setSetpoint()

virtual void YbCtrl::Algorithm::setSetpoint ( double setpoint ) [pure virtual]

Sets the setpoint.

Change setpoint, smoothly if possible.

Parameters
in | setpoint | The new setpoint, from -1 to +1

Implemented in YbCtrl::PIDAlgorithm.

The documentation for this class was generated from the following file:

- Algorithm.h

### 11.2 YbCtrl::Controller Class Reference

Object to manage the locking loop.

#include <Controller.h>

Public Member Functions

- Controller ()
Constuct an empty Controller.
- Controller (ErrorChannel ∗errorInt, CtrlChannel ∗ctrlInt, Algorithm ∗algorithm) Constuct a Controller.
- operator bool () const

### 16 CONTENTS

Is this Controller valid?
- void reset ()
Wipe this Controller.
- int doLoop ()
Do a locking cycle.
- CtrlChannel ∗ getCtrlChannel () Gets the control channel.
- ErrorChannel ∗ getErrorInterface () Gets the error interface.
- Algorithm ∗ getAlgorithm ()
Gets the algorithm.
- int replaceCtrlChannel (bool)
Remove the current CtrlChannel.
- int replaceCtrlChannel (CtrlChannel ∗newInterface) Replace the current CtrlChannel.
- char ∗ reportState (char ∗ptr)
Reports the state.

### 11.2.1 Detailed Description

Object to manage the locking loop.

This object manages pointers to an ErrorChannel, a CtrlChannel and an Algorithm.

It uses these objects to get the error signal, calculate a new output level and send that output every time doLoop() is called.

This object can be marked as valid or invalid. It is considered invalid if any of its three contained objects are a) not present or b) themselves marked invalid.

### 11.2.2 Constructor & Destructor Documentation

### 11.2.2.1 Controller() [1/2]

YbCtrl::Controller::Controller ( )
Constuct an empty Controller.

This empty controller is marked invalid.

### 11.2.2.2 Controller() [2/2]

YbCtrl::Controller::Controller ( ErrorChannel ∗ errorInt,
CtrlChannel ∗ ctrlInt,
Algorithm ∗ algorithm )
Constuct a Controller.

Constuct a controller using pointers to its substituents. This is the recommended constructor form.

N.B. a CtrlChannel may only be assigned to a single Controller at a time. To ensure this, a pointer is placed within the CtrlChannel to its controlling Controller, if it exists. This constuctor checks for the presence of this pointer and, if it points to another rival Controller, it refuses to use the passed CtrlChannel and this Controller is marked invalid.

11.2 YbCtrl::Controller Class Reference | 17

Parameters
in | errorInt | The error interface
in | ctrlInt | The control interface
in | algorithm | The algorithm

### 11.2.3 Member Function Documentation

### 11.2.3.1 doLoop()

int YbCtrl::Controller::doLoop ( )

Do a locking cycle.

Does one cycle of the loop. Reads error, performs calculation and outputs result

Returns
Returns 0 (error code not implemented)

### 11.2.3.2 getAlgorithm()

Algorithm∗ YbCtrl::Controller::getAlgorithm ( ) [inline]

Gets the algorithm.

Returns
The algorithm.

### 11.2.3.3 getCtrlChannel()

CtrlChannel∗ YbCtrl::Controller::getCtrlChannel ( ) [inline]

Gets the control channel.

Returns
The control channel.

### 18 CONTENTS

### 11.2.3.4 getErrorInterface()

ErrorChannel∗ YbCtrl::Controller::getErrorInterface ( ) [inline]

Gets the error interface.

Returns
The error interface.

### 11.2.3.5 operator bool()

YbCtrl::Controller::operator bool ( ) const [explicit]

Is this Controller valid?

Return true if the ErrorInterface, CtrlChannel and Algorithm are all present and valid. Otherwise return false.

### 11.2.3.6 replaceCtrlChannel() [1/2]

int YbCtrl::Controller::replaceCtrlChannel ( bool ) [inline]

Remove the current CtrlChannel.

Calls replaceCtrlChannel() with a null pointer.

Parameters
in | <unnamed> | Any bool. Value is ignored

Returns
Error codes

Return values
0 Success

### 11.2.3.7 replaceCtrlChannel() [2/2]

int YbCtrl::Controller::replaceCtrlChannel ( CtrlChannel ∗ newInterface ) [inline]

Replace the current CtrlChannel.

Replaces the current CtrlChannel with a new one, releasing control of the current CtrlChannel.

11.2 YbCtrl::Controller Class Reference | 19

Parameters
in | newInterface | The new CtrlChannel

Returns
Error codes

Return values
0 | Success
1 | Error: new CtrlChannel is already assigned.

### 11.2.3.8 reportState()

char∗ YbCtrl::Controller::reportState ( char ∗ ptr ) [inline]

Reports the state.

Write into ptr a string that identifies the currently running loop. This is delegated to the Algorithm

Parameters
out | ptr | Pointer to a buffer. Should hold at least 128 chars.

Returns
Returns ptr

### 11.2.3.9 reset()

void YbCtrl::Controller::reset ( )

Wipe this Controller.

Relinquishes control of the current CtrlChannel and wipes all parameters.

The documentation for this class was generated from the following files:

- Controller.h
- Controller.cpp

### 20 CONTENTS

### 11.3 YbCtrl::CtrlChannel Class Reference

Abstract object to allow outputting a control signal.

#include <CtrlChannel.h>

Inheritance diagram for YbCtrl::CtrlChannel:

YbCtrl::CtrlChannel

YbCtrl::V4_OPA_OutputChannel

YbCtrl::V4_OPA_OutputChannelBipolar

Public Member Functions

- virtual double recallCtrl ()=0
Read out the current output.
- virtual CtrlChannelReturn setLimits (double minimum, double maximum) final Set software limits on the max/min ctrl signal.
- virtual operator bool () const =0
Is this object valid?
- virtual CtrlChannelReturn setCurrentLimit (double val) Limits the current.
- virtual double getCurrentLimit ()
Gets the current limit.
- virtual CtrlChannelReturn isOverheated (bool &state)
Check for overheated.
- virtual CtrlChannelReturn getLimits (double &min, double &max)=0 Gets the output limits.
- virtual CtrlChannelReturn getCurrentLimit (double &out)
Gets the current limit.
- virtual void setCtrl (double val) final
Sets the control signal.
- void setContainingController (Controller ∗newController) Sets the containing Controller.
- Controller ∗ getContainingController ()
Gets the containing Controller.
- CtrlChannelReturn getContainingController (Controller ∗&out)
Gets the containing controller.
- CtrlChannelReturn addConflictingChannel (CtrlChannel ∗newConflict) Adds a conflicting channel.
- CtrlChannelReturn closeConflictingControllers ()
Closes conflicting controllers.

11.3 YbCtrl::CtrlChannel Class Reference | 21

### 11.3.1 Detailed Description

Abstract object to allow outputting a control signal.

This object is a tempate for class that writes an output to the real world. Child classes will implement specifics, e.g. writing a voltage to an OPA.

As with the Algorithm class, this class is abstract and so derived classes must override many of its methods.

For an example, see V4_OPA_OutputChannel.

### 11.3.2 Member Function Documentation

### 11.3.2.1 addConflictingChannel()

CtrlChannelReturn YbCtrl::CtrlChannel::addConflictingChannel ( CtrlChannel ∗ newConflict ) [inline]

Adds a conflicting channel.

Adds a channel that is considered to be conflicting with this one. I.e. this channel and the conflicting one should not be simultaneously controlled.

This is useful e.g. for bipolar vs. single-sided channels which use the same outputs.

Up to 2 channels can be added using this function. Any Controllers associated with these channels can be closed with closeConflictingControllers

Returns
Error code

### 11.3.2.2 closeConflictingControllers()

CtrlChannelReturn YbCtrl::CtrlChannel::closeConflictingControllers ( )

Closes conflicting controllers.

Close any Controllers that are managing either this channel or any conflicting ones. Conflicting channels are identified by adding pointers to them with addConflictingChannel.

Note
Similarily to setCtrl() vs writeCtrl(), this is the public interface which is defined by the base class. The derived classes will overwrite the private pure virtual member writeLimits() which is called by this function and which will actually set the limits.

Returns
Error code

### 22 CONTENTS

### 11.3.2.3 getContainingController() [1/2]

Controller∗ YbCtrl::CtrlChannel::getContainingController ( ) [inline]

Gets the containing Controller.

Returns
The containing controller. NULL if none present.

### 11.3.2.4 getContainingController() [2/2]

CtrlChannelReturn YbCtrl::CtrlChannel::getContainingController ( Controller ∗& out ) [inline]

Gets the containing controller.

Parameters
out | out | The containing Controller

Returns
Error code

### 11.3.2.5 getCurrentLimit() [1/2]

virtual double YbCtrl::CtrlChannel::getCurrentLimit ( ) [inline], [virtual]

Gets the current limit.

Gets the current limit. Value in amps

Returns
The current limit in amps. -999 if not implemented

Reimplemented in YbCtrl::V4_OPA_OutputChannel.

### 11.3.2.6 getCurrentLimit() [2/2]

virtual CtrlChannelReturn YbCtrl::CtrlChannel::getCurrentLimit ( double & out ) [inline], [virtual]

Gets the current limit.

Gets the current limit and stores it in out. Value in amps

11.3 YbCtrl::CtrlChannel Class Reference | 23

Parameters
out | out | The current limit in amps

Returns
Error code

Reimplemented in YbCtrl::V4_OPA_OutputChannel.

### 11.3.2.7 getLimits()

virtual CtrlChannelReturn YbCtrl::CtrlChannel::getLimits ( double & min,
double & max ) [pure virtual]

Gets the output limits.

Store the output limits in the passed references.

Parameters
out | min | The minimum
out | max | The maximum

Returns
Error code

Implemented in YbCtrl::V4_OPA_OutputChannel.

### 11.3.2.8 isOverheated()

virtual CtrlChannelReturn YbCtrl::CtrlChannel::isOverheated ( bool & state ) [inline], [virtual]

Check for overheated.

Check if this channel is overheated

Parameters
out | state | True if overheated, false otherwise

### 24 CONTENTS

Returns
Error return

Reimplemented in YbCtrl::V4_OPA_OutputChannel, and YbCtrl::V4_OPA_OutputChannelBipolar.

### 11.3.2.9 operator bool()

virtual YbCtrl::CtrlChannel::operator bool ( ) const [explicit], [pure virtual]

Is this object valid?

Return true if this object has been constucted with valid parameters

Implemented in YbCtrl::V4_OPA_OutputChannel.

### 11.3.2.10 recallCtrl()

virtual double YbCtrl::CtrlChannel::recallCtrl ( ) [pure virtual]

Read out the current output.

Read out the current output. Values from -1 to 1.

Returns
Current ctrl level

Implemented in YbCtrl::V4_OPA_OutputChannel.

### 11.3.2.11 setContainingController()

void YbCtrl::CtrlChannel::setContainingController ( Controller ∗ newController ) [inline]

Sets the containing Controller.

Set this object's managing Controller to the given target

Parameters
newController The new managing Controller

### 11.3.2.12 setCtrl()

void YbCtrl::CtrlChannel::setCtrl (

11.3 YbCtrl::CtrlChannel Class Reference | 25

double val ) [final], [virtual]

Sets the control signal.

Set the control signal to the given value. Also, if this channel is managed by a Controller, inform that Controller's Algorithm of the updated output level

Note
This method is declared in an external object file. This is necessary because, at the point of including this header file, the Controller object has not yet been fully defined. Since setCtrl() uses methods in Controller, it cannot be compiled until Controller is fully defined. Therefore the code must be in a .cpp file, to be compiled later after all the headers are resolved.

See the documentation for setLimits for an explaination as to why this structure is needed

Parameters
val The value, from -1 to +1

### 11.3.2.13 setCurrentLimit()

virtual CtrlChannelReturn YbCtrl::CtrlChannel::setCurrentLimit ( double val ) [inline], [virtual]

Limits the current.

If implemented, limit the current to the given value.

N.B. this method DOES NOT use -1 -> +1 notation; the input is in amps.

Parameters
in | val | The current limit in Amps

Returns
Error code

Reimplemented in YbCtrl::V4_OPA_OutputChannel, and YbCtrl::V4_OPA_OutputChannelBipolar.

### 11.3.2.14 setLimits()

CtrlChannelReturn YbCtrl::CtrlChannel::setLimits ( double minimum,
double maximum ) [final], [virtual]
Set software limits on the max/min ctrl signal.

Also, if this channel is managed by a Controller, inform that Controller's Algorithm of the new limits

### 26 CONTENTS

Note
This method is defined in an external object file. This is necessary because, at the point of including this header file, the Controller object has not yet been fully defined. Since setCtrl() uses methods in Controller, it cannot be compiled until Controller is fully defined. Therefore the code must be in a .cpp file, to be compiled later after all the headers are resolved.
Similarily to setCtrl() vs writeCtrl(), this is the public interface which is defined by the base class. The derived classes will overwrite the private pure virtual member writeLimits() which is called by this function and which will actually set the limits.

Parameters
in | minimum | The new minimum
in | maximum | The new maximum

Returns
Error status

The documentation for this class was generated from the following files:

- CtrlChannel.h
- CtrlChannel.cpp

### 11.4 YbCtrl::ErrorChannel Class Reference

Abstract object to allow measuring an error signal.

#include <ErrorChannel.h>

Inheritance diagram for YbCtrl::ErrorChannel:

YbCtrl::ErrorChannel

YbCtrl::V4_ADC_ChannelPair

Public Member Functions

- virtual double recallError ()=0
Recall error signal.
- virtual ErrorChannelReturn recallError (double &output)=0 Recall error signal.
- virtual bool readInProgress ()
Check if there's a read in progress by this channel.
- virtual bool globalReadInProgress ()
Check if there's a read in progress globally.
- virtual bool readingReady ()
Check if the current reading is ready.

11.4 YbCtrl::ErrorChannel Class Reference | 27
- virtual bool readingTimeout ()
Check if the current reading is has timed out.
- virtual void abortReading ()
Aborts a reading currently in progress.
- virtual ErrorChannelReturn startReading ()
Start reading.
- virtual ErrorChannelReturn getReading (double &readingOutput)=0 Get the latest reading.
- virtual operator bool () const =0
Is this object valid?

### 11.4.1 Detailed Description

Abstract object to allow measuring an error signal.

This object is a tempate for class that reads an input from the real world. Child classes will implement specifics, e.g. reading a voltage from an ADC.

As with the Algorithm class, this class is abstract and so derived classes must override many of its methods.

For an example, see V4_ADC_ChannelPair.

### 11.4.2 Member Function Documentation

### 11.4.2.1 abortReading()

virtual void YbCtrl::ErrorChannel::abortReading ( ) [inline], [virtual]
Aborts a reading currently in progress.

If a reading is in progress, abort it, If not, do nothing

Child objects should either override all of readInProgress, readingReady, readingTimeout and startReading or none of them.

Reimplemented in YbCtrl::V4_ADC_ChannelPair.

### 11.4.2.2 getReading()

virtual ErrorChannelReturn YbCtrl::ErrorChannel::getReading ( double & readingOutput ) [pure virtual]
Get the latest reading.

Gets the completed reading and stores it in readingOutput. The reading uses the format -1 -> +1, where -1 corresponds to the minimum value the ErrorChannel can read and vice versa.

If no conversion is in progress / the conversion failed, return an error message.

Otherwise return ErrorChannelReturn::NO_ERROR.

This method must be overridden by child objects.

### 28 CONTENTS

Parameters
out | readingOutput | Output variable for the reading.

Returns
ErrorChannelReturn error code.

Implemented in YbCtrl::V4_ADC_ChannelPair.

### 11.4.2.3 globalReadInProgress()

virtual bool YbCtrl::ErrorChannel::globalReadInProgress ( ) [inline], [virtual]

Check if there's a read in progress globally.

Returns true if a reading has been started with startReading, has not been aborted with abortReading and has not been returned by getReading BY ANY ErrorChannel.

Otherwise returns false

Before it is overridden, this function always returns true. This is so that simple ErrorChannels that do not require this start / check / read method can instead just return a value from getReading each time.

Child objects should either override all of readInProgress, readingReady, readingTimeout and startReading or none of them.

Returns
true / false

Reimplemented in YbCtrl::V4_ADC_ChannelPair.

### 11.4.2.4 operator bool()

virtual YbCtrl::ErrorChannel::operator bool ( ) const [explicit], [pure virtual]

Is this object valid?

Return true if this object has been constucted with valid parameters

Implemented in YbCtrl::V4_ADC_ChannelPair.

11.4 YbCtrl::ErrorChannel Class Reference | 29

### 11.4.2.5 readingReady()

virtual bool YbCtrl::ErrorChannel::readingReady ( ) [inline], [virtual]

Check if the current reading is ready.

Returns true if a reading has been started with startReading, has not been aborted with abortReading, has not been returned by getReading and has successfully completed

Otherwise returns false

Before it is overridden, this function always returns true. This is so that simple ErrorChannels that do not require this start / check / read method can instead just return a value from getReading each time.

Child objects should either override all of readInProgress, readingReady, readingTimeout and startReading or none of them.

Returns
true / false

Reimplemented in YbCtrl::V4_ADC_ChannelPair.

### 11.4.2.6 readingTimeout()

virtual bool YbCtrl::ErrorChannel::readingTimeout ( ) [inline], [virtual]

Check if the current reading is has timed out.

Returns true if a reading has been started with startReading, has not been aborted with abortReading, has not been returned by getReading, has not successfully completed and has exceeded a maximum timeout.

Otherwise returns false

Before it is overridden, this function always returns false. This is so that simple ErrorChannels that do not require this start / check / read method can instead just return a value from getReading each time.

Child objects should either override all of readInProgress, readingReady, readingTimeout and startReading or none of them.

Returns
true / false

Reimplemented in YbCtrl::V4_ADC_ChannelPair.

### 30 CONTENTS

### 11.4.2.7 readInProgress()

virtual bool YbCtrl::ErrorChannel::readInProgress ( ) [inline], [virtual]

Check if there's a read in progress by this channel.

Returns true if a reading has been started with startReading, has not been aborted with abortReading and has not been returned by getReading BY THIS ErrorChannel

Otherwise returns false

Before it is overridden, this function always returns true. This is so that simple ErrorChannels that do not require this start / check / read method can instead just return a value from getReading each time.

Child objects should either override all of readInProgress, readingReady, readingTimeout and startReading or none of them.

Returns
true / false

Reimplemented in YbCtrl::V4_ADC_ChannelPair.

### 11.4.2.8 recallError() [1/2]

virtual double YbCtrl::ErrorChannel::recallError ( ) [pure virtual]

Recall error signal.

Read out the last measured error. Values from -1 to 1.

Returns
Last measured error signal from -1 to +1

Implemented in YbCtrl::V4_ADC_ChannelPair.

### 11.4.2.9 recallError() [2/2]

virtual ErrorChannelReturn YbCtrl::ErrorChannel::recallError ( double & output ) [pure virtual]

Recall error signal.

Read out the last measured error into output. Values from -1 to 1.

Parameters
out | output | Target for the error signal

11.5 YbCtrl::PIDAlgorithm Class Reference | 31

Returns
Error code

Implemented in YbCtrl::V4_ADC_ChannelPair.

### 11.4.2.10 startReading()

virtual ErrorChannelReturn YbCtrl::ErrorChannel::startReading ( ) [inline], [virtual]

Start reading.

Start a new reading if none in progress (by this channel or globally).

If a reading is already in progress, abort it and start another one.

Child objects should either override all of readInProgress, readingReady, readingTimeout and startReading or none of them.

Returns
ErrorChannelReturn error code.

Reimplemented in YbCtrl::V4_ADC_ChannelPair.

The documentation for this class was generated from the following file:

- ErrorChannel.h

### 11.5 YbCtrl::PIDAlgorithm Class Reference

Implementation of an Algorithm to perform a PID lock.

#include <PIDAlgorithm.h>

Inheritance diagram for YbCtrl::PIDAlgorithm:

YbCtrl::PIDAlgorithm

YbCtrl::Algorithm

### 32 CONTENTS

Public Member Functions
- PIDAlgorithm (double K, double Ti, double Td, double initialOutput, double target=0, double N=10, bool disableProportional=false)
Constuctor.
- PIDAlgorithm ()
Alternative constuctor.
- bool lockingAlgo () override
Does this algorithm lock?
- operator bool () override
Returns true if this object has been initialised with valid parameters.
- double output (double input) override
Do the PID calculation.
- void setOutput (double output) override
Sets the output.
- void setSetpoint (double setpoint) override
Sets the setpoint.
- void setLimits (double min, double max) override Sets output limits.
- double getSetpoint () override
Gets the setpoint.

Protected Member Functions
- char ∗ reportState (char ∗ptr) override Report state.

### 11.5.1 Detailed Description

Implementation of an Algorithm to perform a PID lock.
An implementation of Algorithm that performs a PID lock based on the parameters passed during its constuction. The lock performed by this object implements the following transfer function:

G(s) = −K
1 +

1
sTI

+

sTD
1 + sTD
N

!

When created without parameters passed to the consructor, this object will be marked invalid. This allows the user to reserve space on the stack, while still recording which PIDAlgorithms are properly setup.
As usual, all inputs / outputs are to be given in -1 to +1 format.

### 11.5.2 Constructor & Destructor Documentation

### 11.5.2.1 PIDAlgorithm() [1/2]

YbCtrl::PIDAlgorithm::PIDAlgorithm ( double K,
double Ti,
double Td,
double initialOutput,
double target = 0,
double N = 10,
bool disableProportional = false )
Constuctor.

11.5 YbCtrl::PIDAlgorithm Class Reference | 33

Parameters
in | K | Proportional gain
in | Ti | Integral time constant
in | Td | Differential time constant
in | initialOutput | The initial output
in | target | The target error signal
in | N | High frequency damping coefficient. ∼10 is a good value.
in | disableProportional | Disable proportional gain
in | timingCycles | To speed up execution, the PID parameters are recalulated according to the measured loop speed every timingCycles loops.
in | debug | Enable debug output

### 11.5.2.2 PIDAlgorithm() [2/2]

YbCtrl::PIDAlgorithm::PIDAlgorithm ( ) [inline]

Alternative constuctor.

A PIDAlgorithm constructed without parameters is marked invalid. This can be useful for reserving stack space for these objects, allowing them to be declared in advance.

E.g.

PIDAlgorithm algos[3];

bool valid = algos[1]; // returns false

algos[1] = PIDALgorithm(1,1,0,0,0);

bool valid = algos[1]; // returns true

### 11.5.3 Member Function Documentation

### 11.5.3.1 getSetpoint()

double YbCtrl::PIDAlgorithm::getSetpoint ( ) [inline], [override], [virtual]

Gets the setpoint.

Returns
The current setpoint.

Implements YbCtrl::Algorithm.

### 34 CONTENTS

### 11.5.3.2 lockingAlgo()

bool YbCtrl::PIDAlgorithm::lockingAlgo ( ) [inline], [override], [virtual]

Does this algorithm lock?

Returns a boolean describing whether this Algorithm implementation locks or not. E.g. the PIDAlgorithm, a derived implementation of this class, does lock so it overrides this method with

return true;

Currently there are no examples of Algorithms that do not lock.

Returns
true / false

Reimplemented from YbCtrl::Algorithm.

### 11.5.3.3 output()

double YbCtrl::PIDAlgorithm::output ( double input ) [override], [virtual]

Do the PID calculation.

See p242 of http://www.cds.caltech.edu/∼murray/courses/cds101/fa02/caltech/astrom-ch6.←-pdf for an in depth explaination of how this works

Parameters
in | input | The current error signal input. Values from -1 to +1

Returns
The calculated new ctrl signal. Values from -1 to +1

Implements YbCtrl::Algorithm.

### 11.5.3.4 reportState()

char∗ YbCtrl::PIDAlgorithm::reportState ( char ∗ ptr ) [inline], [override], [protected], [virtual]

Report state.

Send a string that identifies the currently running algorithm.

11.5 YbCtrl::PIDAlgorithm Class Reference | 35

Parameters
out | ptr | A buffer to contain the output. Should be at least 128 chars long.

Returns
Returns ptr

Implements YbCtrl::Algorithm.

### 11.5.3.5 setLimits()

void YbCtrl::PIDAlgorithm::setLimits ( double min,
double max ) [override], [virtual]

Sets output limits.

Set limits on the algorithm's output. Values are from -1 to +1.

Parameters
in | min | The new minimum
in | max | The new maximum

Implements YbCtrl::Algorithm.

### 11.5.3.6 setOutput()

void YbCtrl::PIDAlgorithm::setOutput ( double output ) [override], [virtual]

Sets the output.

Set the output to a specified level, smoothly if possible.

Parameters
in | output | The new output, from -1 to +1.

Implements YbCtrl::Algorithm.

### 11.5.3.7 setSetpoint()

void YbCtrl::PIDAlgorithm::setSetpoint ( double setpoint ) [override], [virtual]

### 36 CONTENTS

Sets the setpoint.

Change setpoint, smoothly if possible.

Parameters
in | setpoint | The new setpoint, from -1 to +1

Implements YbCtrl::Algorithm.

The documentation for this class was generated from the following files:

- PIDAlgorithm.h
- PIDAlgorithm.cpp

### 11.6 pinToggler< numPins > Class Template Reference

Class for toggling pins.

#include <pinToggler.h>

Inherits pinTogglerBase.

Static Public Member Functions

- static int init (const uint8_t ∗LED_Pins)

Initiate the pins and TIMER1
- static int setFlashRate (const size_t LED, const FLASHRATE rate) Change the flash rate of an LED managed by this routine.
- static int getPin (const size_t LED)

Return the pin corresponding to a given LED
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

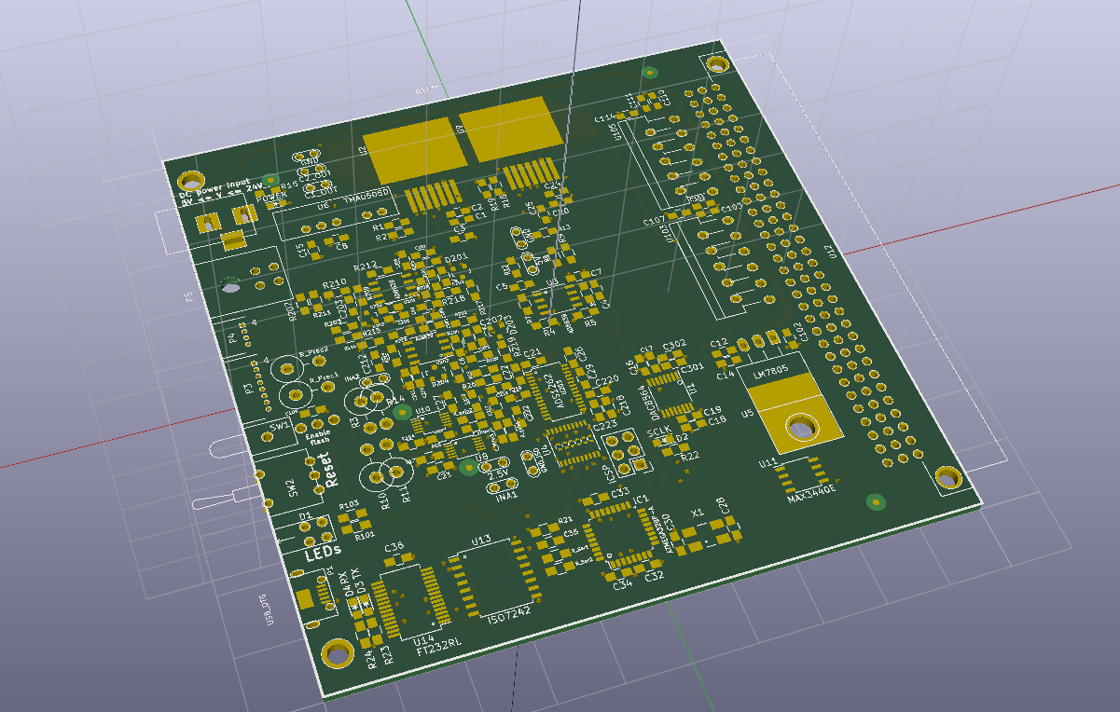
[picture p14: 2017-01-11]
Manual/images/WholeBoard.png

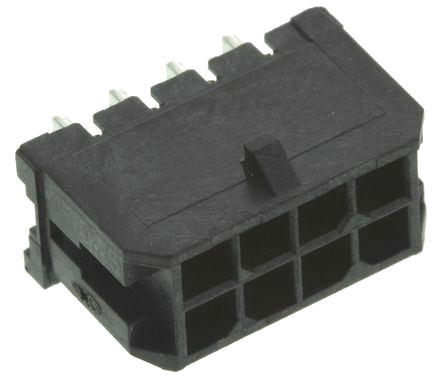
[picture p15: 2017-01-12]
Manual/images/Microfit/MicroFit8.png

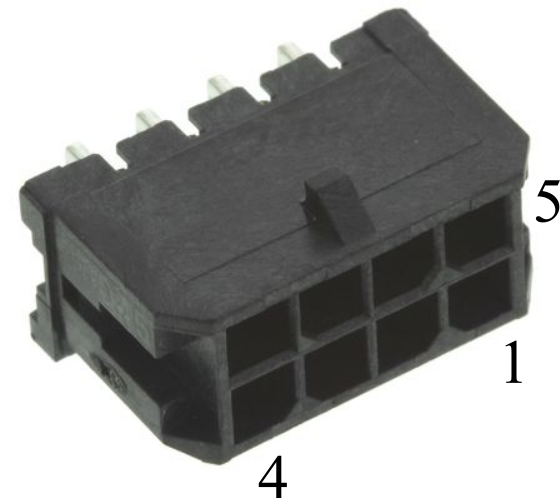
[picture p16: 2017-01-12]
Manual/images/Microfit.png

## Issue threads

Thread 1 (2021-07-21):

### ISSUE TITLE
Error in commands

### ISSUE THREAD

**Issue by QiushuoSun** [charlesbaynham/DigitalTemperatureController#1]
Hi Charles,

I am a research fellow in Sr atoms group at the University of Birmingham. One of my colleagues recommended your design for temperature controllers for high finesse cavities. Thank you very much for providing this design and all the documents!

I have got some PCBs manufactured based on your design, and I have established the communication between the microcontroller and a computer. However, I am having issues with some commands.

The first issue is the Error in startup commands. This error shows up first every time the board is connected.

The second issue is the Error in some of the commands. I found the error only shows up for all the commands that the number of parameters is not 0.

I attached a picture here to give some examples, the first line shows the startup error. The second line is when I sent *TST and I got 'loud and clear' in return without an issue. The third line is when I sent 'LOCK' command but got an error.

![temp](https://user-images.githubusercontent.com/86027181/122376464-161ef300-cf5c-11eb-9e45-9abb1246aaee.PNG)

I don't have much experience in C++ or Arduino, if you could help with any ideas, that would be very helpful!

Also please can I ask should I use Labview files as a user interface, once I have got the C++ programme running?

Again, thank you very much for the design, and I appreciate any answers.

Best regards,
Sarah

**Comment by han94ros** [comment]
Hi Charles 

I am Sarah's colleague, and the issue was that in your VoltageLock C++ function you have defined the CtrlChannel as the first parameter followed by the ErrorChannel as the second. The order is reversed for the documentation of the LOCK arduino command in the manual. You can close this issue now.

**Comment by charlesbaynham** [comment]
Hello both, 

Great to hear you're using the board! Thanks for finding this documentation error, I'll get that sorted out. 

For future reference, the CommandHandlerReturn codes come from here: 

https://github.com/charlesbaynham/DigitalTemperatureController/blob/82d15f1a2f9fbe171d7a6bbacd06541c10ce3214/Code_for_microcontroller/YbTempCtrl/CommandHandler/CommandHandler.h#L29-L43

So e.g. error 1 means "command not found" and error 2 means "wrong number of params". 

For controlling the board you'll find a Labview interface here: https://github.com/charlesbaynham/DigitalTemperatureController/tree/master/Code%20for%20Labview. This includes a driver which implements most of the serial commands, as well as a basic GUI (which might be a bit buggy: sorry!). I'd probably recommend using either the labview driver VIs or implementing a simple one in python. Another package I've written might help with this: https://github.com/charlesbaynham/GenericSCPIDriver/. 

Let me know if you have any other question!
C

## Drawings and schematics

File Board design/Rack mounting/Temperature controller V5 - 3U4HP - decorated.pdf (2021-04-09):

E | E
F | F

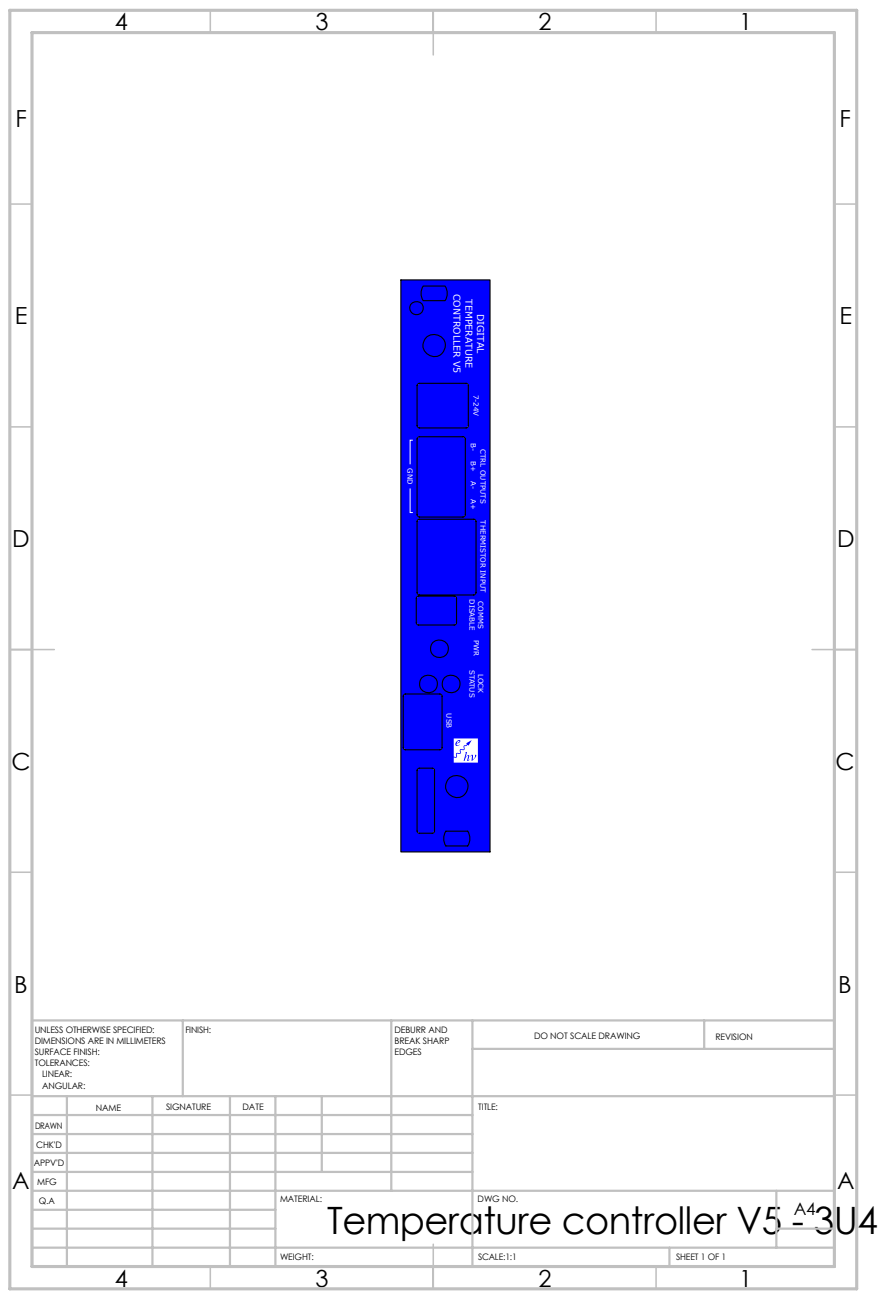
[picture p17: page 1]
FINISH:; DEBURR AND; BREAK SHARP EDGES; DO NOT SCALE DRAWING; REVISION; SCALE:1:1; SHEET 1 OF 1; WEIGHT:; Temperature controller V5 - 3U4 DIGITAL TEMPERATURE CONTROLLER V5; 7-24V CTRL OUTPUTS B- B+ A- A+ THERMISTOR INPUT DISABLE COMMS PWR LOCK STATUS USB GND

UNLESS OTHERWISE SPECIFIED:
DIMENSIONS ARE IN MILLIMETERS
SURFACE FINISH:
TOLERANCES:
LINEAR:
ANGULAR:

NAME | SIGNATURE | DATE | | | | TITLE:

DRAWN
CHK'D
APPV'D
MFG
Q.A | | | | MATERIAL: | DWG NO. | A4

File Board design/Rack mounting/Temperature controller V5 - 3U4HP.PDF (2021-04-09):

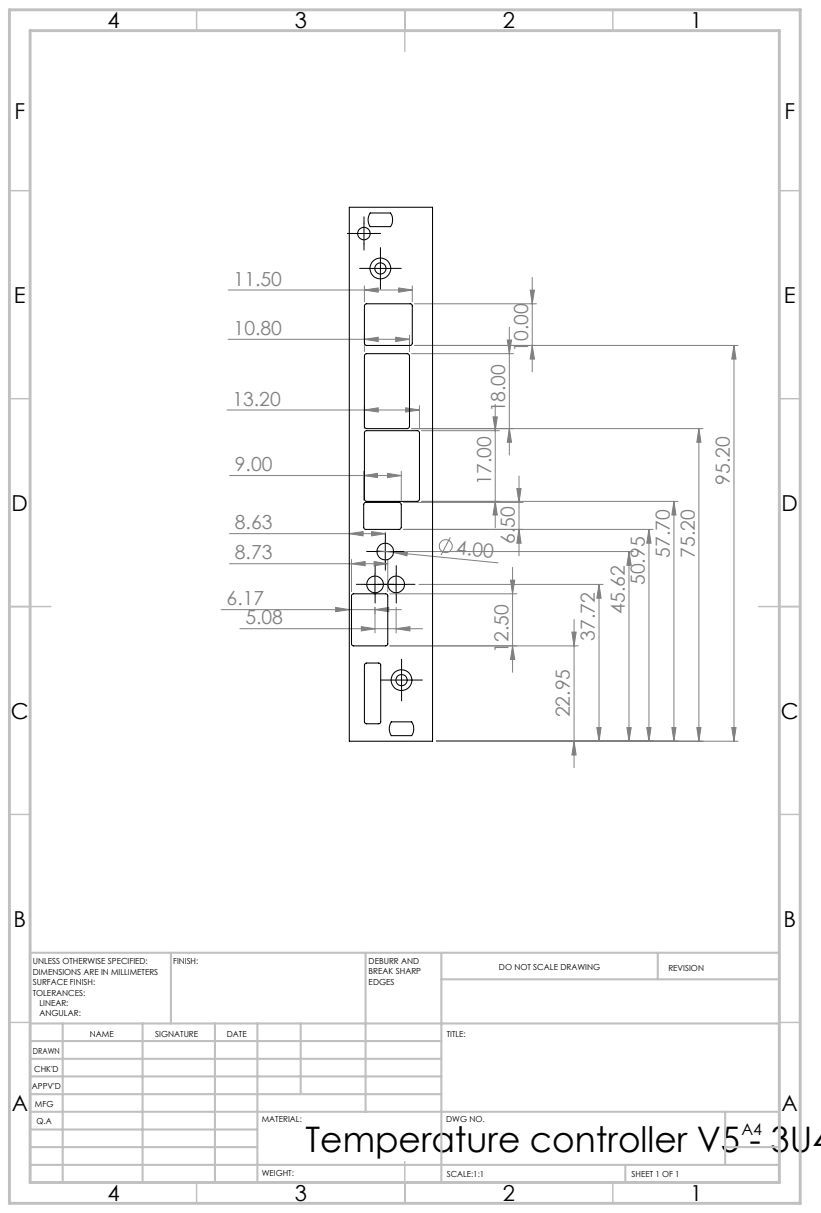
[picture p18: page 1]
FINISH:; DEBURR AND; BREAK SHARP; DO NOT SCALE DRAWING; REVISION; SCALE:1:1; SHEET 1 OF 1; Temperature controller V5 - 3U4HP

UNLESS OTHERWISE SPECIFIED:
DIMENSIONS ARE IN MILLIMETERS
SURFACE FINISH:
TOLERANCES:
LINEAR:
ANGULAR:

NAME | SIGNATURE | DATE | | | | TITLE:

DRAWN
CHK'D
APPV'D
MFG
Q.A | | | | MATERIAL: | DWG NO. | A4

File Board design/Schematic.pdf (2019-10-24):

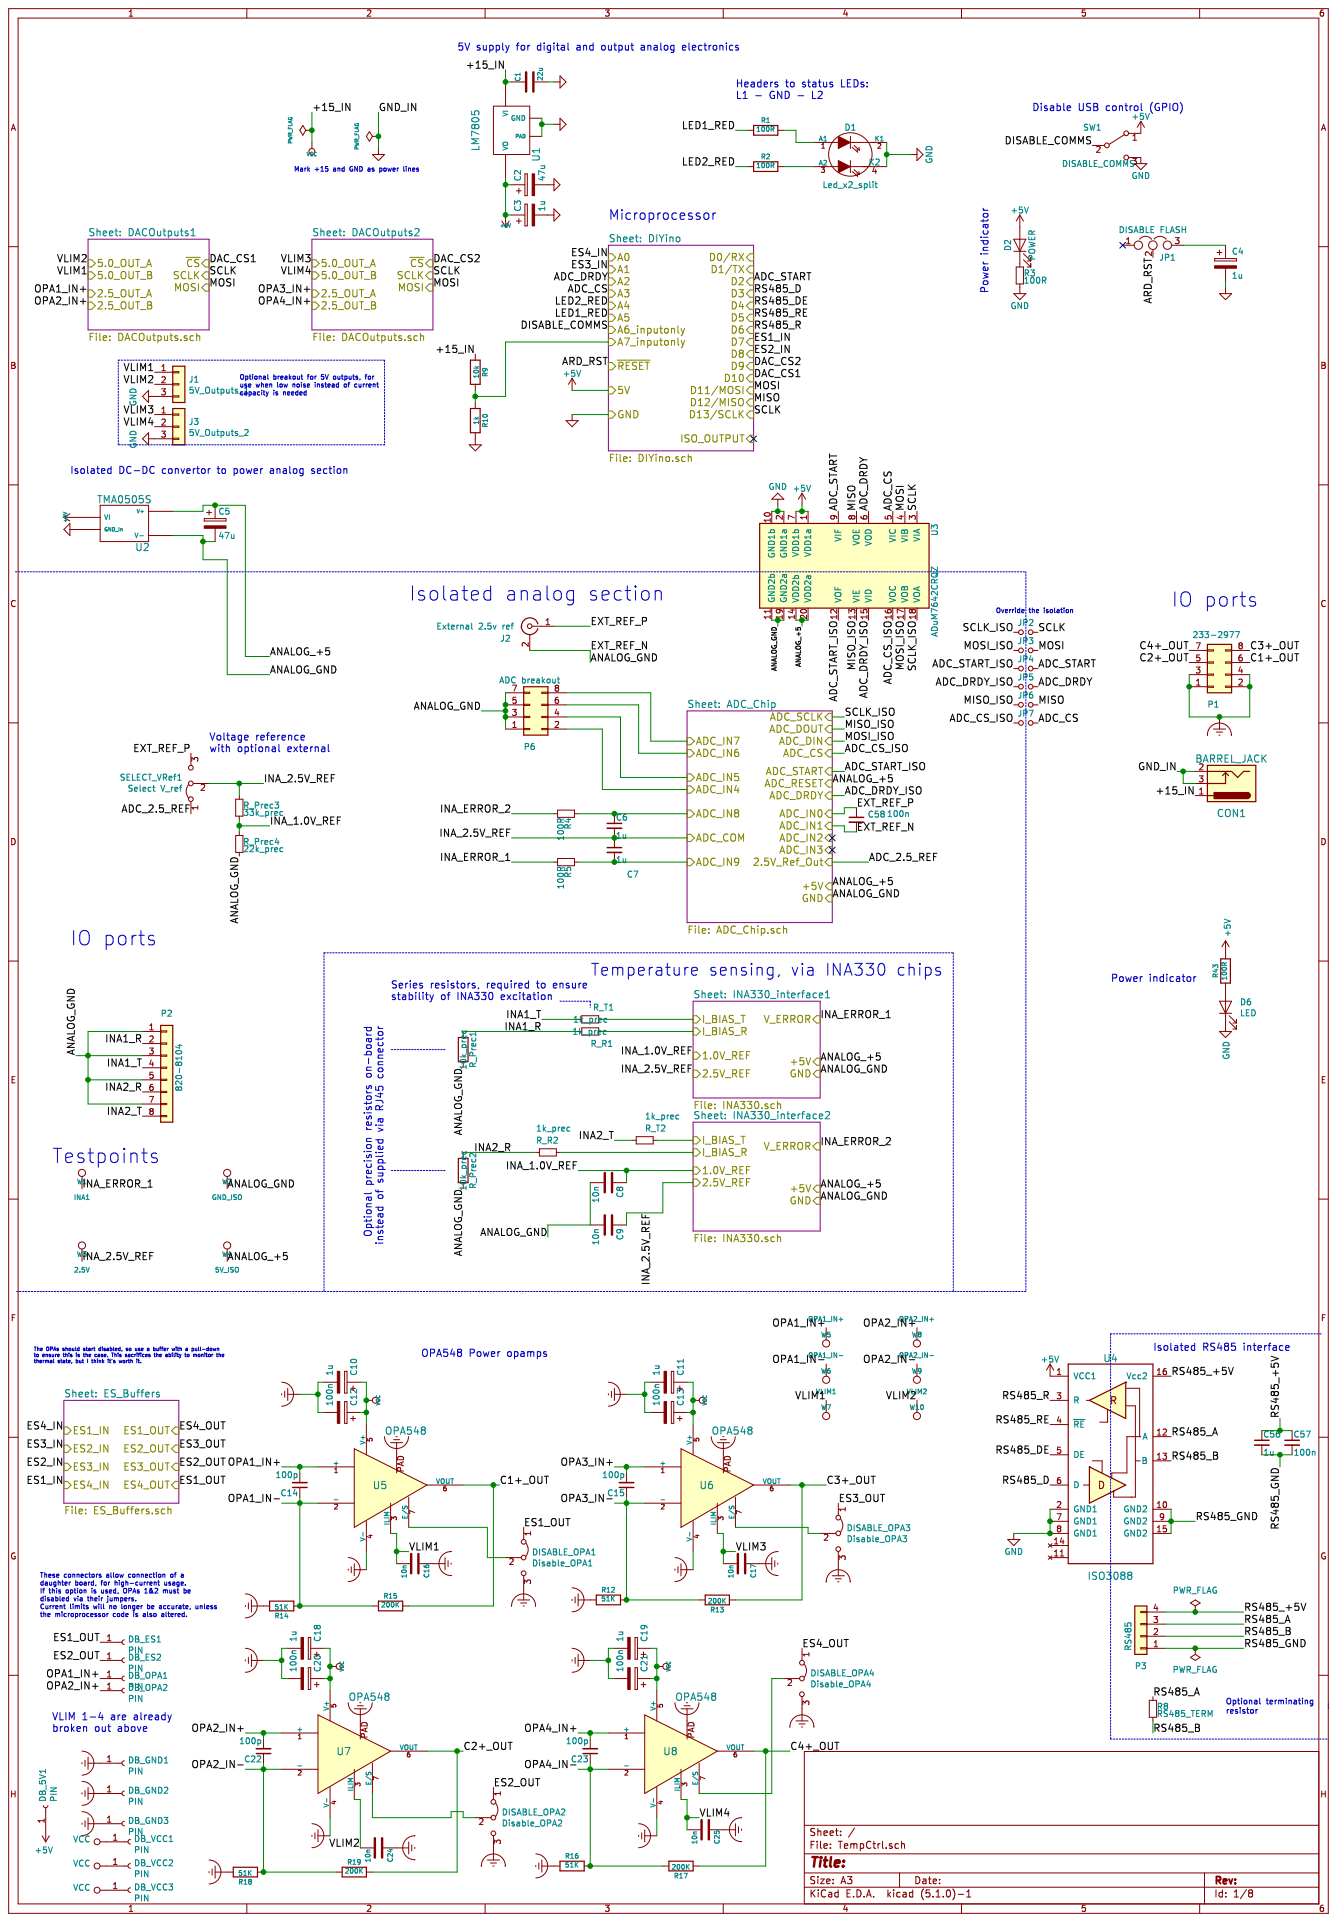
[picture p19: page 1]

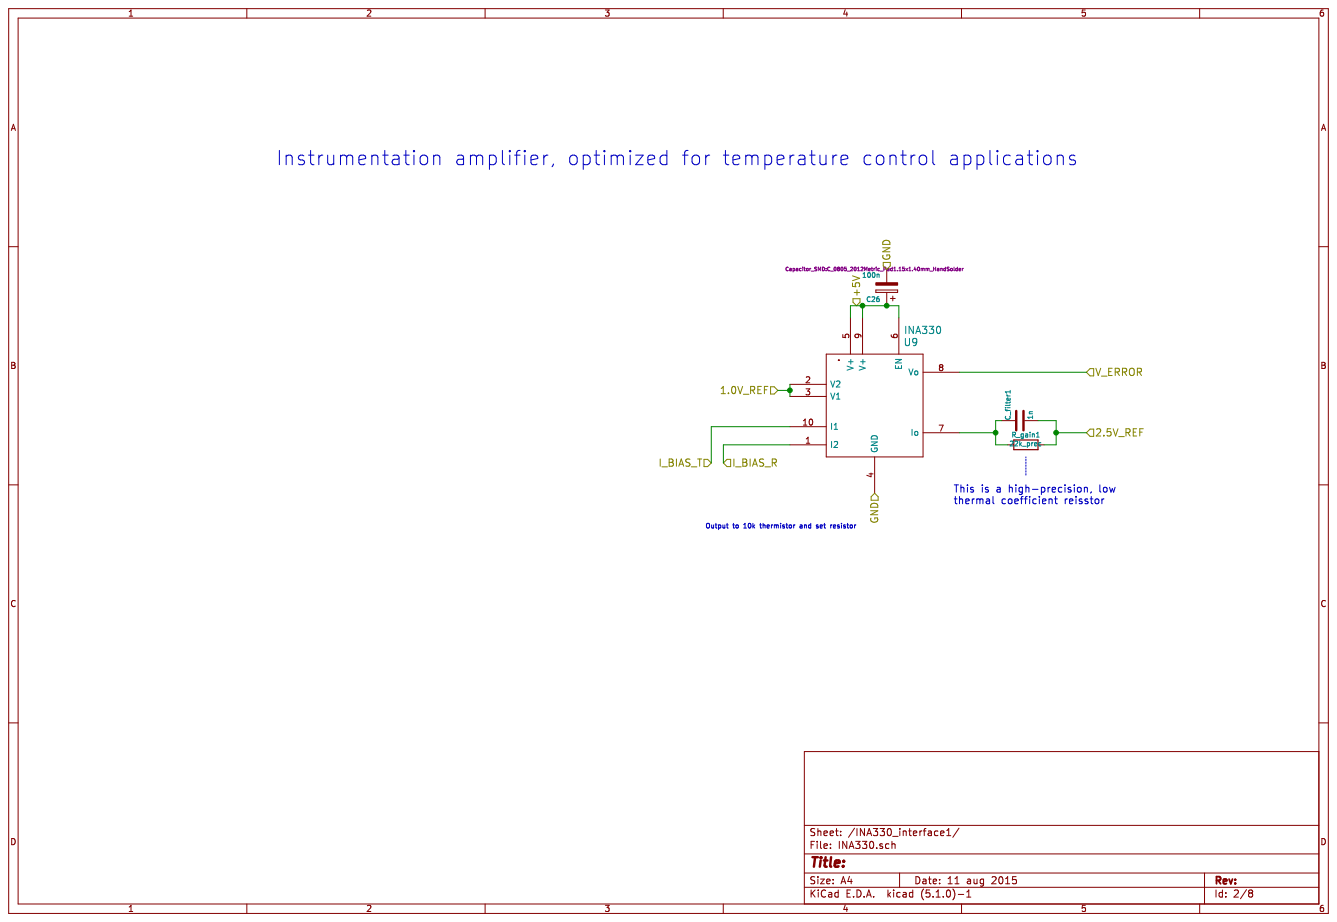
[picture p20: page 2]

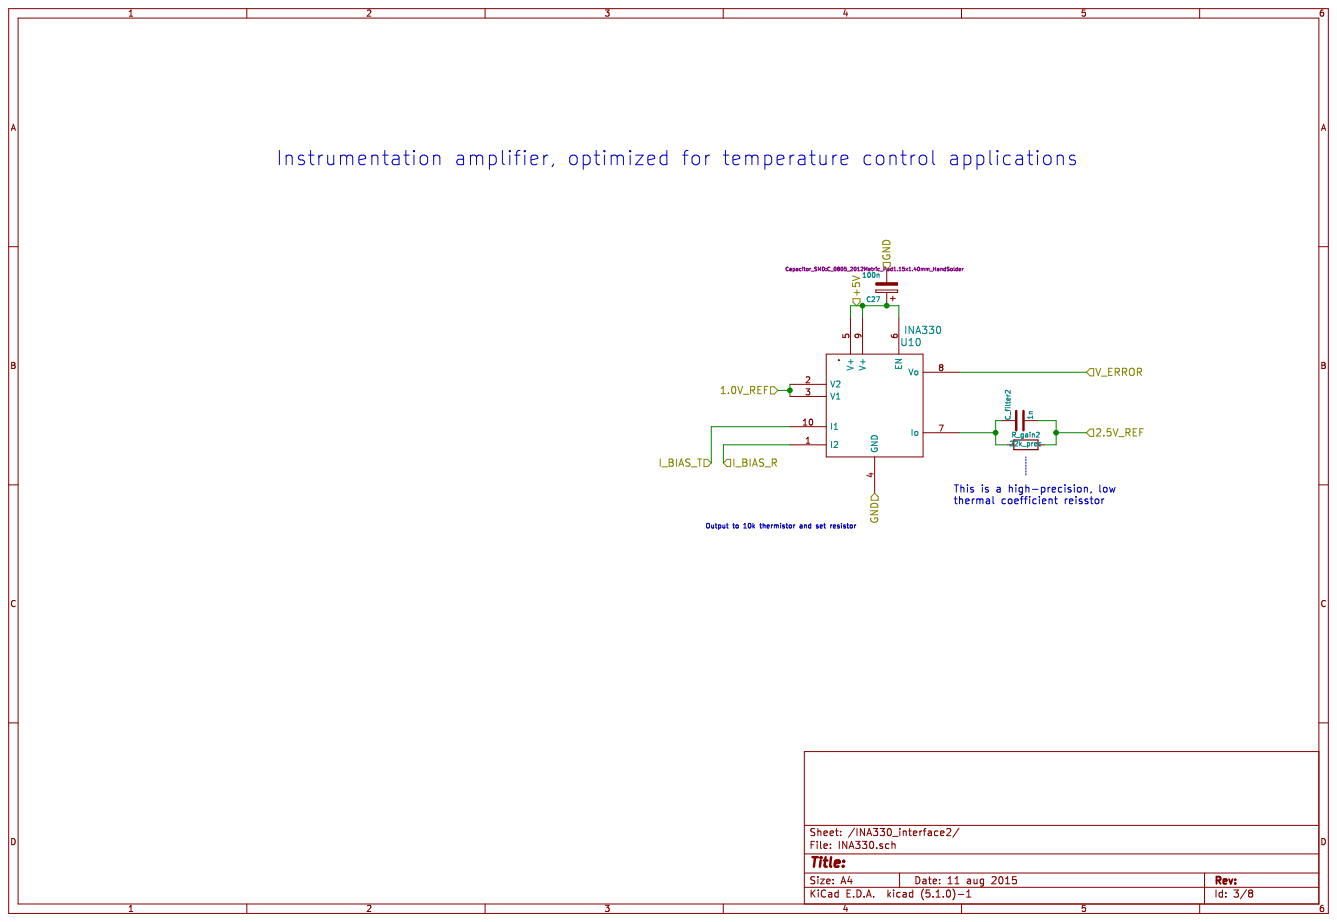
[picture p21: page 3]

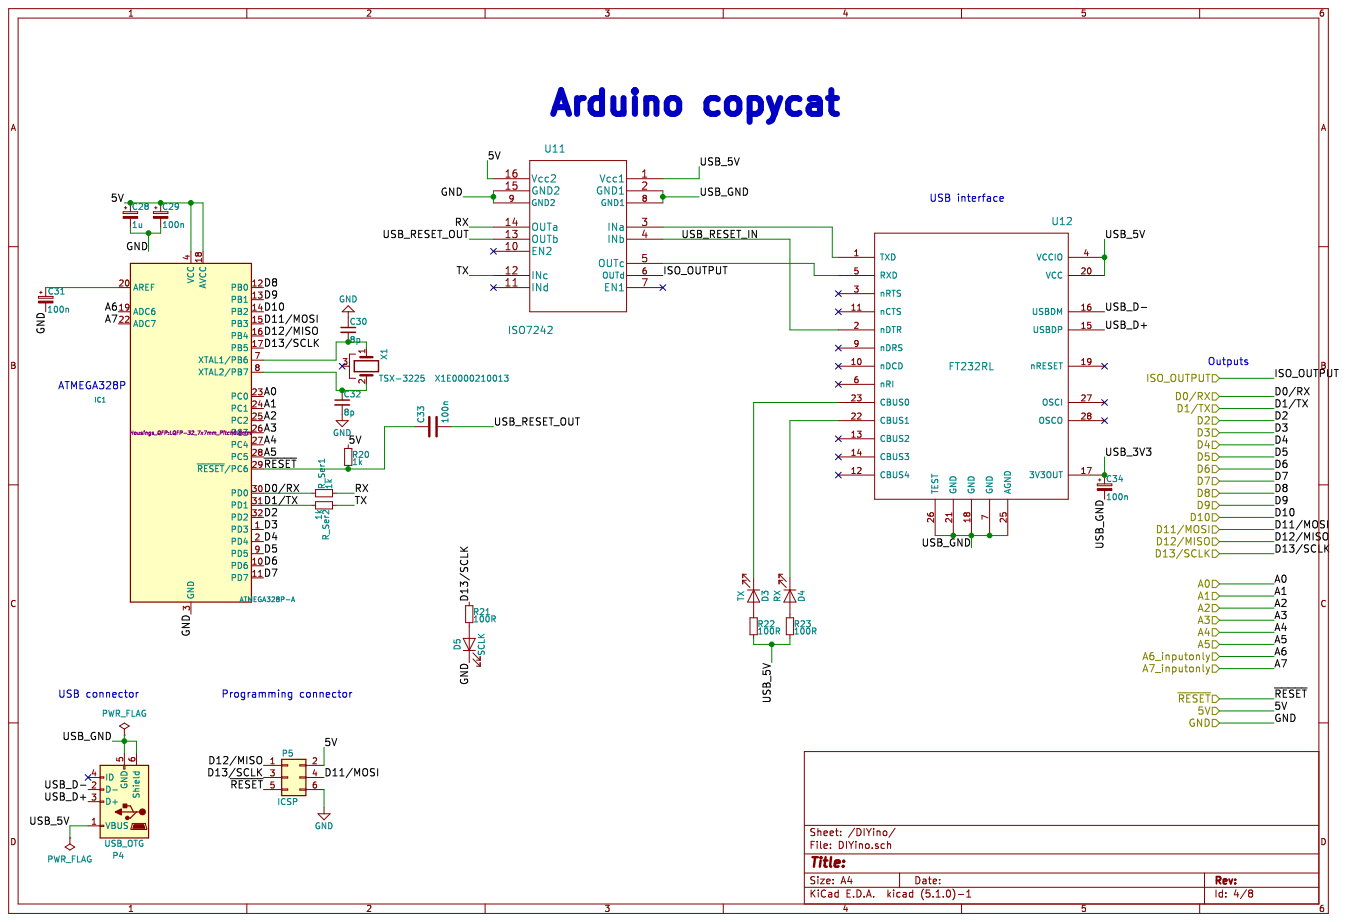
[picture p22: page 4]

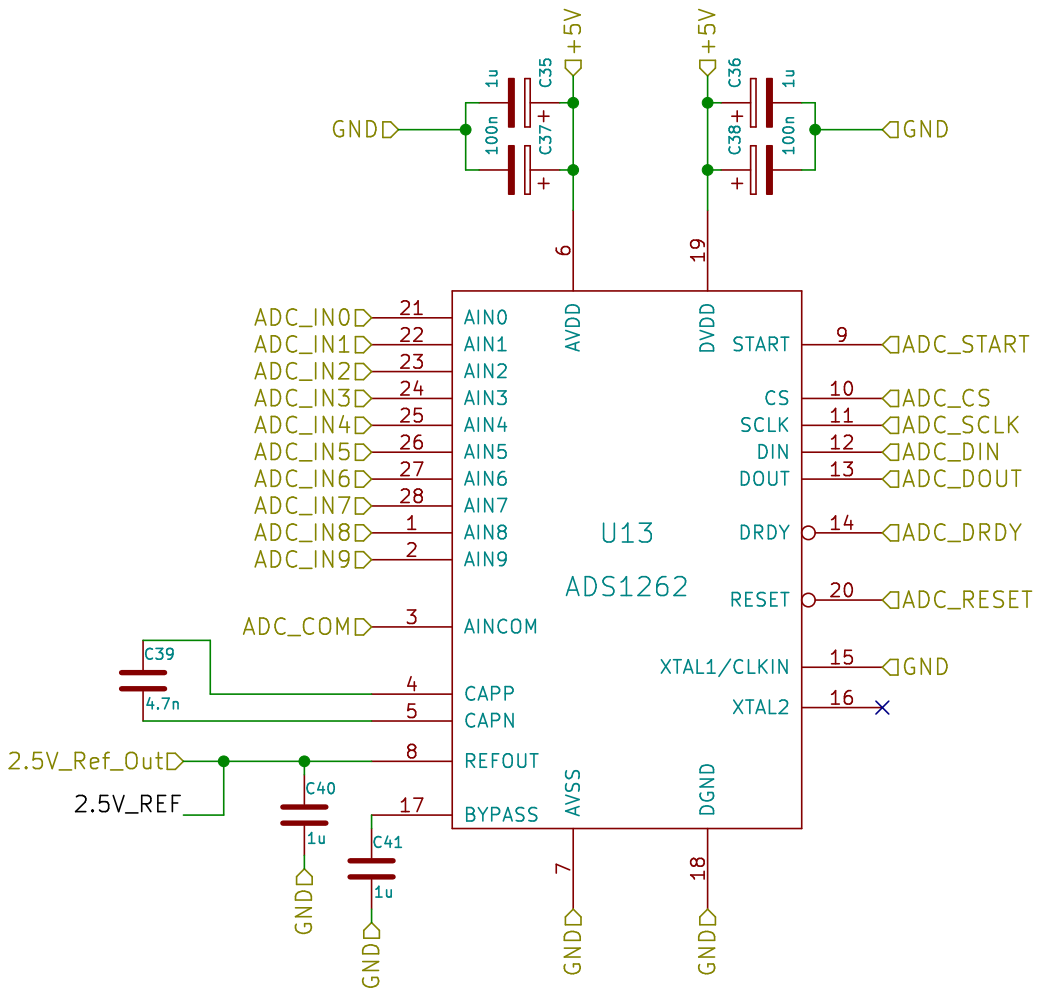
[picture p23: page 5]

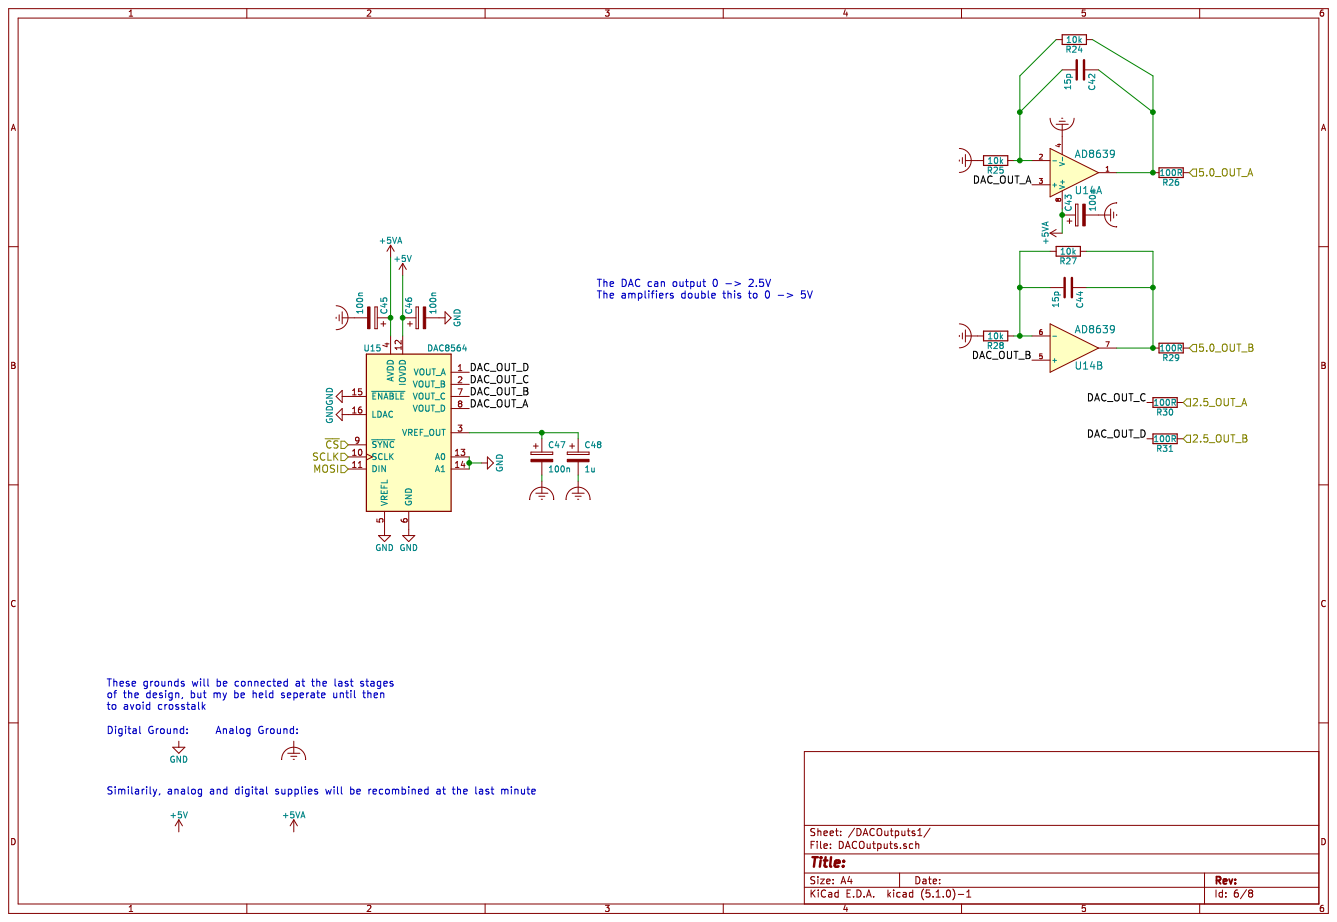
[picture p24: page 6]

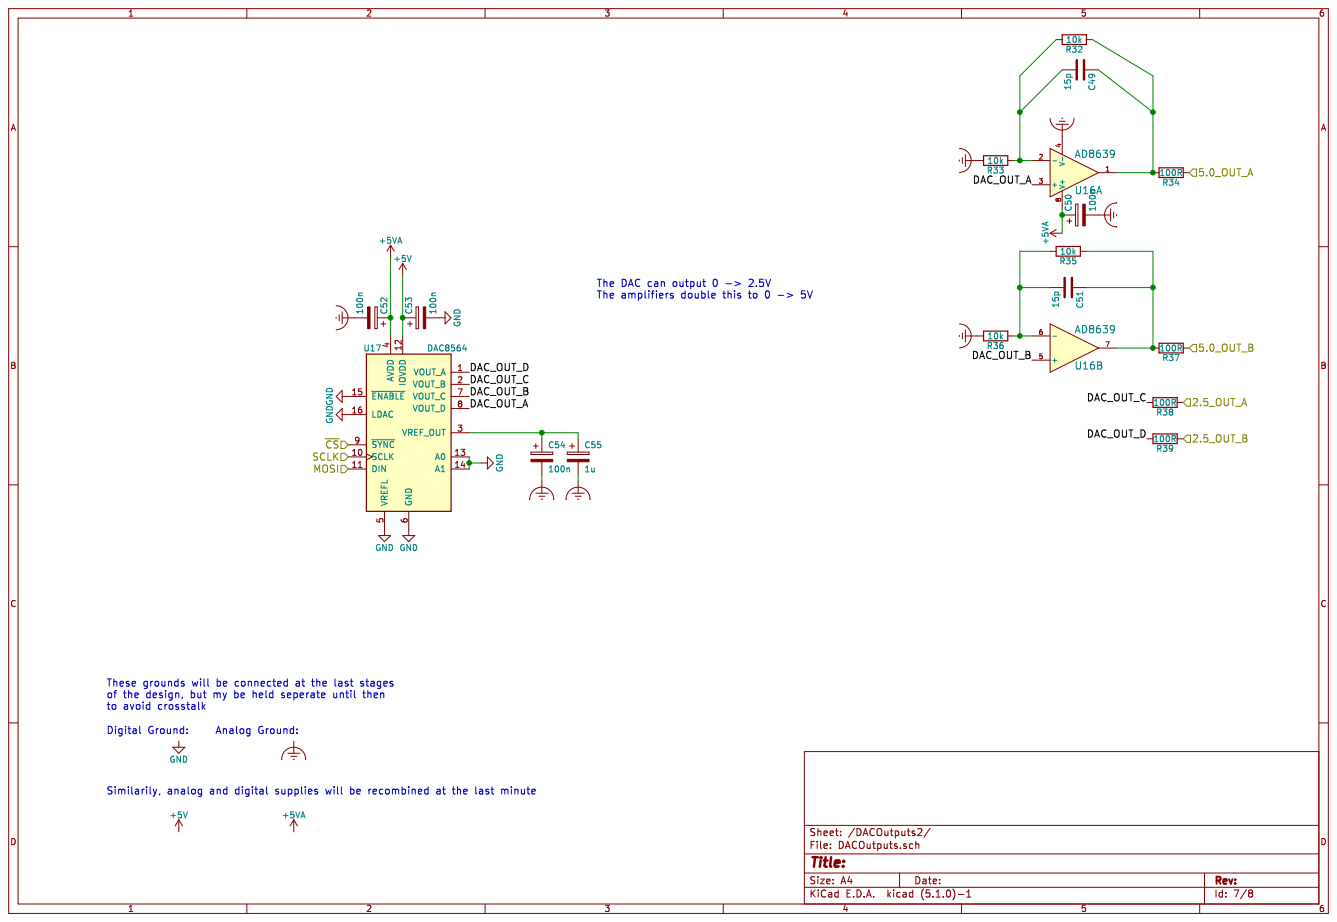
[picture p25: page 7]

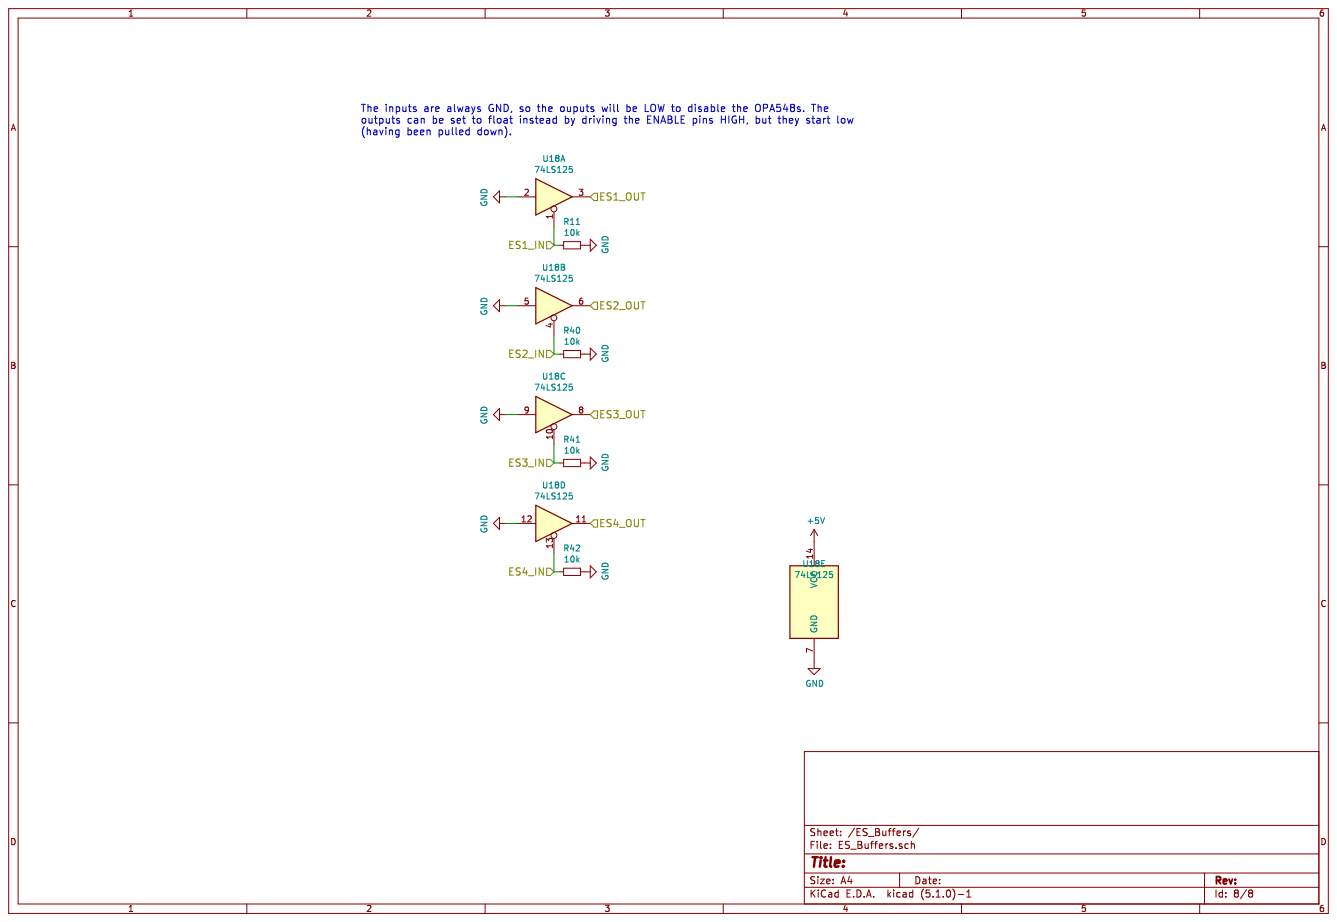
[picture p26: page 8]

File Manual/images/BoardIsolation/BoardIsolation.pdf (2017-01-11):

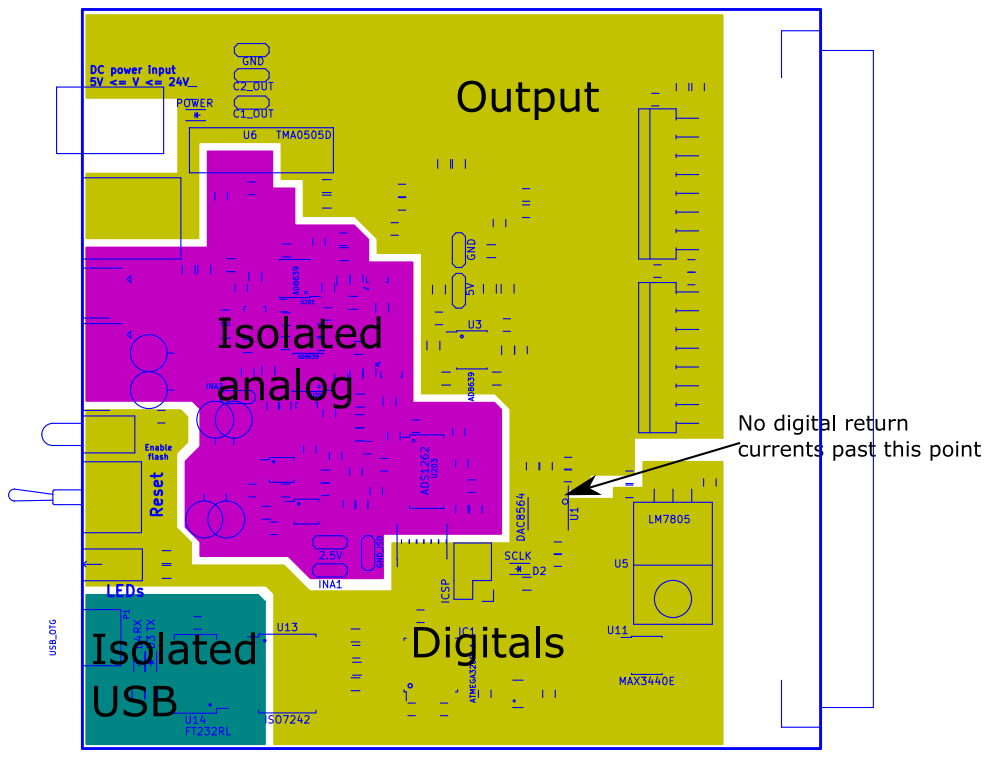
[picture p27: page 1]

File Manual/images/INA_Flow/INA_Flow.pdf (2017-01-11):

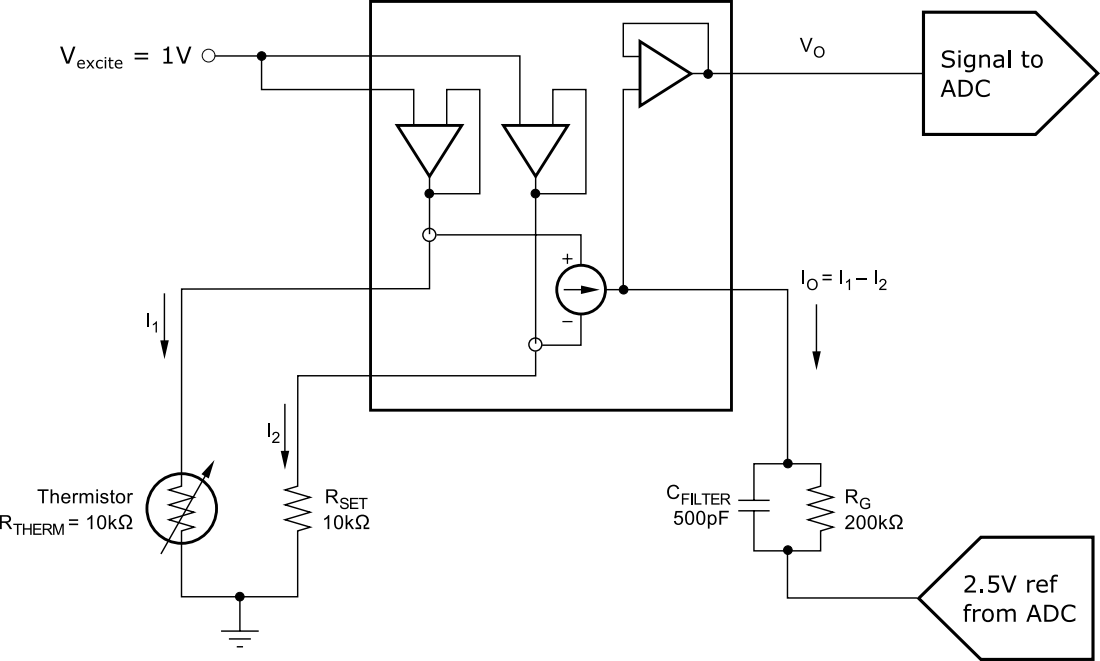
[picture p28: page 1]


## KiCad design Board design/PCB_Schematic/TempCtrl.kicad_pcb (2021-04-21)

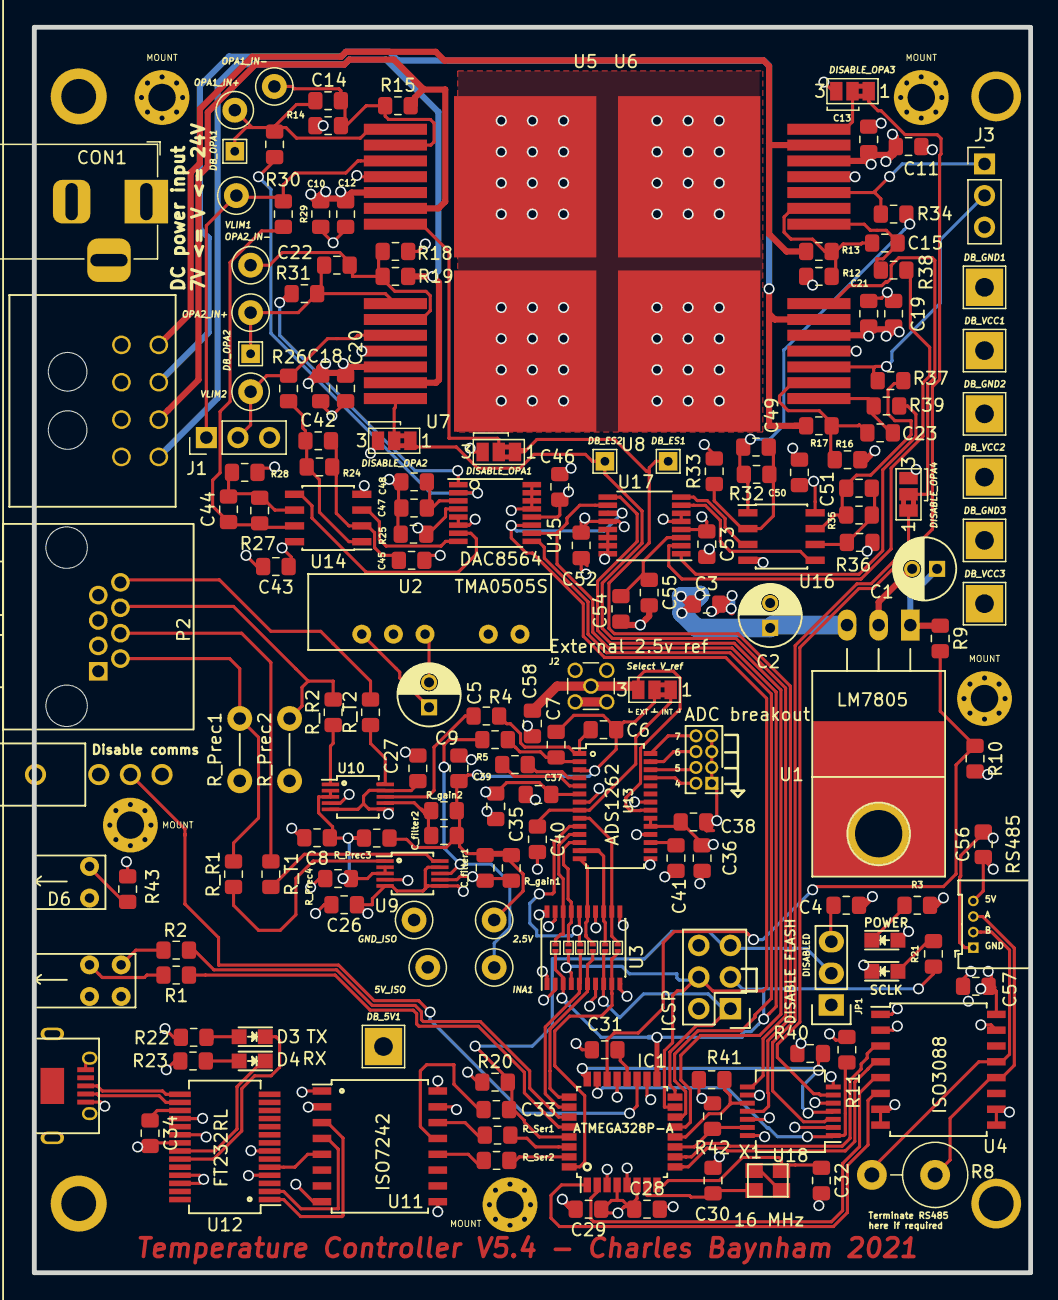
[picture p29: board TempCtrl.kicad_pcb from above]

Board: 4 copper layers, 80.0 x 100.0 mm, 184 parts (0 on the bottom side), 129 nets.

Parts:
C1: 22u; C_Radial_D5_L11_P2
C2, C5: 47u; C_Radial_D5_L11_P2
C3, C4, C6, C7, C10, C11, C18, C19, C28, C35, C36, C40, C41, C48, C55, C56: 1u; C_0805_2012Metric_Pad1.15x1.40mm_HandSolder
C8, C9: 10n; C_0805_2012Metric_Pad1.15x1.40mm_HandSolder
C12, C13, C20, C21, C26, C27, C29, C31, C33, C34, C37, C38, C43, C45, C46, C47, C50, C52, C53, C54, C57, C58: 100n; C_0805_2012Metric_Pad1.15x1.40mm_HandSolder
C14, C15, C22, C23: 100p; C_0805_2012Metric_Pad1.15x1.40mm_HandSolder
C30, C32: 8p; C_0805_2012Metric_Pad1.15x1.40mm_HandSolder
C39: 4.7n; C_0805_2012Metric_Pad1.15x1.40mm_HandSolder
C42, C44, C49, C51: 15p; C_0805_2012Metric_Pad1.15x1.40mm_HandSolder
CON1: BARREL_JACK; BarrelJack_Horizontal
C_filter1, C_filter2: 1n; C_0805_2012Metric_Pad1.15x1.40mm_HandSolder
D1: Led_x2_split; Double_LEDs
D2: POWER; LED_0805
D3: TX; LED_0805
D4: RX; LED_0805
D5: SCLK; LED_0805
D6: LED; PCB_MOUNT_LED
DB_5V1: PIN; TestPoint_THTPad_3.0x3.0mm_Drill1.5mm
DB_ES1, DB_ES2: PIN; TestPoint_THTPad_1.5x1.5mm_Drill0.7mm
DB_GND1, DB_GND2, DB_GND3: PIN; TestPoint_THTPad_3.0x3.0mm_Drill1.5mm
DB_OPA1, DB_OPA2: PIN; TestPoint_THTPad_1.5x1.5mm_Drill0.7mm
DB_VCC1, DB_VCC2, DB_VCC3: PIN; TestPoint_THTPad_3.0x3.0mm_Drill1.5mm
DISABLE_OPA1: Disable_OPA1; SolderJumper-3_P1.3mm_Bridged2Bar12_Pad1.0x1.5mm_NumberLabe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
DISABLE_OPA2: Disable_OPA2; SolderJumper-3_P1.3mm_Bridged2Bar12_Pad1.0x1.5mm_NumberLabe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
DISABLE_OPA3: Disable_OPA3; SolderJumper-3_P1.3mm_Bridged2Bar12_Pad1.0x1.5mm_NumberLabe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
DISABLE_OPA4: Disable_OPA4; SolderJumper-3_P1.3mm_Bridged2Bar12_Pad1.0x1.5mm_NumberLabe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
IC1: ATMEGA328P-A; LQFP-32_7x7mm_Pitch0.8mm
J1: 5V_Outputs_1; PinHeader_1x03_P2.54mm_Vertical
J2: External 2.5v ref; MMCX_Molex_73415-1471_Vertical
J3: 5V_Outputs_2; PinHeader_1x03_P2.54mm_Vertical
JP1: DISABLE FLASH; Pin_Header_Straight_1x03
JP2, JP3, JP4, JP5, JP6, JP7: Jumper_NO_Small; SmallJumperNoCourtyard
MOUNT: MountingHole_2.2mm_M2_Pad_Via
MOUNT#2, MOUNT#3, MOUNT#4, MOUNT#5: MountingHole_2.2mm_M2_Pad_Via
P1: 233-2977; Molex_Microfit3_Header_02x04_Angled_43045-080x_FIXED
P2: 820-8104; RJ45_TE
P3: RS485; Molex_PicoBlade_53048-0410_04x1.25mm_Angled
P4: USB_OTG; MICRO-B_USB_TOP_MOUNT
P5: ICSP; 6pin_3x2_Amphenol_75869-131LF
P6: ADC breakout; Pin_Header_Straight_2x04_Pitch1.27mm
R1, R2, R3, R4, R5, R21, R22, R23, R26, R29, R30, R31, R34, R37, R38, R39, R43: 100R; R_0805_2012Metric_Pad1.15x1.40mm_HandSolder
R8: RS485_TERM; R_Axial_DIN0516_L15.5mm_D5.0mm_P5.08mm_Vertical
R9, R11, R24, R25, R27, R28, R32, R33, R35, R36, R40, R41, R42: 10k; R_0805_2012Metric_Pad1.15x1.40mm_HandSolder
R10, R20: 1k; R_0805_2012Metric_Pad1.15x1.40mm_HandSolder
R12, R14, R16, R18: 51K; R_0805_2012Metric_Pad1.15x1.40mm_HandSolder
R13, R15, R17, R19: 200K; R_0805_2012Metric_Pad1.15x1.40mm_HandSolder
R_Prec1, R_Prec2: 10k_prec; Resistor_Vertical_RM5mm_Cust
R_Prec3: 33k_prec; R_0805_2012Metric_Pad1.15x1.40mm_HandSolder
R_Prec4: 22k_prec; R_0805_2012Metric_Pad1.15x1.40mm_HandSolder
R_R1, R_R2: 1k_prec; R_0805_2012Metric_Pad1.15x1.40mm_HandSolder
R_Ser1, R_Ser2: 1k; R_0805_2012Metric_Pad1.15x1.40mm_HandSolder
R_T1, R_T2: 1k_prec; R_0805_2012Metric_Pad1.15x1.40mm_HandSolder
R_gain1, R_gain2: 22k_prec; R_0805_2012Metric_Pad1.15x1.40mm_HandSolder
SELECT_VRef1: Select V_ref; SolderJumper-3_P1.3mm_Bridged2Bar12_Pad1.0x1.5mm_NumberLabe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
SW1: DISABLE_COMMS; ApemSwitch
U1: LM7805; TO220_HORZ
U2: TMA0505S; SIP_TMA0505
U3: ADuM7642CRQZ; SSOP-20_4.4x6.5mm_Pitch0.65mm
U4: ISO3088; SOIC-16W_7.5x10.3mm_Pitch1.27mm
U5, U6, U7, U8: OPA548; TO-263-7Lead
U9, U10: INA330; MSOP-10_3x3mm_Pitch0.5mm
U11: ISO7242; SOIC-16_7.5x10.3mm_Pitch1.27mm
U12: FT232RL; SSOP-28_5.3x10.2mm_Pitch0.65mm
U13: ADS1262; TSSOP-28_4.4x9.7mm_Pitch0.65mm
U14, U16: AD8639; SOIC-8_3.9x4.9mm_Pitch1.27mm
U15, U17: DAC8564; TSSOP-16_4.4x5mm_Pitch0.65mm
U18: 74LS125; SSOP-14_5.3x6.2mm_P0.65mm
W1: INA1; TestPoint_Loop_D2.50mm_Drill1.0mm
W2: GND_ISO; TestPoint_Loop_D2.50mm_Drill1.0mm
W3: 2.5V; TestPoint_Loop_D2.50mm_Drill1.0mm
W4: 5V_ISO; TestPoint_Loop_D2.50mm_Drill1.0mm
W5: OPA1_IN+; TestPoint_Loop_D2.50mm_Drill1.0mm
W6: OPA1_IN-; TestPoint_Loop_D2.50mm_Drill1.0mm
W7: VLIM1; TestPoint_Loop_D2.50mm_Drill1.0mm
W8: OPA2_IN+; TestPoint_Loop_D2.50mm_Drill1.0mm
W9: OPA2_IN-; TestPoint_Loop_D2.50mm_Drill1.0mm
W10: VLIM2; TestPoint_Loop_D2.50mm_Drill1.0mm
X1: TSX-3225 X1E0000210013; crystal_FA238-TSX3225

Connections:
+5V: C2.1, C3.1, C28.1, C29.1, C43.1, C45.1, C46.1, C50.1, C52.1, C53.1, D2.2, DB_5V1.1, IC1.4, IC1.6, IC1.18, P5.2, R20.1, R43.2, SW1.1, U1.3, U2.1, U3.1, U3.7, U4.1, U11.16, U14.8, U15.4, U15.12, U16.8, U17.4, U17.12, U18.14
/ADC_2.5_REF: C40.1, SELECT_VRef1.1, U13.8
/ADC_CS: IC1.26, JP7.2, U3.5
/ADC_CS_ISO: JP7.1, U3.16, U13.10
/ADC_Chip/ADC_IN4: P6.2, U13.25
/ADC_Chip/ADC_IN5: P6.4, U13.26
/ADC_Chip/ADC_IN6: P6.6, U13.27
/ADC_Chip/ADC_IN7: P6.8, U13.28
/ADC_Chip/ADC_IN8: C6.1, R4.1, U13.1
/ADC_Chip/ADC_IN9: C7.2, R5.1, U13.2
/ADC_DRDY: IC1.25, JP5.2, U3.6
/ADC_DRDY_ISO: JP5.1, U3.15, U13.14
/ADC_START: IC1.32, JP4.2, U3.9
/ADC_START_ISO: JP4.1, U3.12, U13.9
/ANALOG_+5: C5.1, C26.1, C27.1, C35.1, C36.1, C37.1, C38.1, U2.6, U3.14, U3.20, U9.5, U9.6, U9.9, U10.5, U10.6, U10.9, U13.6, U13.19, U13.20, W4.1
/ANALOG_GND: C5.2, C8.2, C9.2, C26.2, C27.2, C35.2, C36.2, C37.2, C38.2, C40.2, C41.2, C58.2, J2.2, P2.1, P2.3, P2.5, P2.7, P6.1, P6.3, P6.5, P6.7, R_Prec1.2, R_Prec2.2, R_Prec4.2, U2.4, U3.11, U3.19, U9.4, U10.4, U13.7, U13.15, U13.18, U13.22, W2.1
/ARD_RST: C33.1, IC1.29, JP1.2, P5.5, R20.2
/C1+_OUT: P1.6, R15.2, U5.6
/C2+_OUT: P1.5, R19.2, U7.6
/C3+_OUT: P1.8, R13.2, U6.6
/C4+_OUT: P1.7, R17.2, U8.6
/DACOutputs1/DAC_OUT_A: U14.3, U15.8
/DACOutputs1/DAC_OUT_B: U14.5, U15.7
/DACOutputs1/DAC_OUT_C: R30.2, U15.2
/DACOutputs1/DAC_OUT_D: R31.2, U15.1
/DACOutputs2/DAC_OUT_A: U16.3, U17.8
/DACOutputs2/DAC_OUT_B: U16.5, U17.7
/DACOutputs2/DAC_OUT_C: R38.2, U17.2
/DACOutputs2/DAC_OUT_D: R39.2, U17.1
/DAC_CS1: IC1.14, U15.9
/DAC_CS2: IC1.13, U17.9
/DISABLE_COMMS: IC1.19, SW1.2
/DIYino/A7_inputonly: IC1.22, R9.2, R10.1
/DIYino/D0/RX: IC1.30, R_Ser1.1
/DIYino/D1/TX: IC1.31, R_Ser2.2
/DIYino/RX: R_Ser1.2, U11.14
/DIYino/TX: R_Ser2.1, U11.12
/DIYino/USB_3V3: C34.1, U12.17
/DIYino/USB_5V: P4.1, R22.2, R23.2, U11.1, U12.4, U12.20
/DIYino/USB_D+: P4.3, U12.15
/DIYino/USB_D-: P4.2, U12.16
/DIYino/USB_GND: C34.2, P4.5, P4.6, U11.2, U11.8, U12.7, U12.18, U12.21, U12.25, U12.26
/DIYino/USB_RESET_IN: U11.4, U12.2
/DIYino/USB_RESET_OUT: C33.2, U11.13
/ES1_IN: IC1.11, R42.2, U18.13
/ES1_OUT: DB_ES1.1, DISABLE_OPA1.1, U18.11
/ES2_IN: IC1.12, R41.2, U18.10
/ES2_OUT: DB_ES2.1, DISABLE_OPA2.1, U18.8
/ES3_IN: IC1.24, R40.2, U18.4
/ES3_OUT: DISABLE_OPA3.1, U18.6
/ES4_IN: IC1.23, R11.2, U18.1
/ES4_OUT: DISABLE_OPA4.1, U18.3
/EXT_REF_P: C58.1, J2.1, SELECT_VRef1.3, U13.21
/INA1_R: P2.2, R_Prec1.1, R_R1.2
/INA1_T: P2.4, R_T1.1
/INA2_R: P2.6, R_Prec2.1, R_R2.2
/INA2_T: P2.8, R_T2.2
/INA330_interface1/I_BIAS_R: R_R1.1, U9.1
/INA330_interface1/I_BIAS_T: R_T1.2, U9.10
/INA330_interface2/I_BIAS_R: R_R2.1, U10.1
/INA330_interface2/I_BIAS_T: R_T2.1, U10.10
/INA_1.0V_REF: C8.1, R_Prec3.2, R_Prec4.1, U9.2, U9.3, U10.2, U10.3
/INA_2.5V_REF: C6.2, C7.1, C9.1, C_filter1.2, C_filter2.2, R_Prec3.1, R_gain1.2, R_gain2.2, SELECT_VRef1.2, U13.3, W3.1
/INA_ERROR_1: R5.2, U9.8, W1.1
/INA_ERROR_2: R4.2, U10.8
/LED1_RED: IC1.28, R1.1
/LED2_RED: IC1.27, R2.1
/MISO: IC1.16, JP6.2, P5.1, U3.8
/MISO_ISO: JP6.1, U3.13, U13.13
/MOSI: IC1.15, JP3.2, P5.4, U3.4, U15.11, U17.11
/MOSI_ISO: JP3.1, U3.17, U13.12
/OPA1_IN+: C14.2, DB_OPA1.1, R30.1, U5.1, W5.1
/OPA1_IN-: C14.1, R14.2, R15.1, U5.2, W6.1
/OPA2_IN+: C22.2, DB_OPA2.1, R31.1, U7.1, W8.1
/OPA2_IN-: C22.1, R18.2, R19.1, U7.2, W9.1
/OPA3_IN+: C15.2, R38.1, U6.1
/OPA3_IN-: C15.1, R12.2, R13.1, U6.2
/OPA4_IN+: C23.2, R39.1, U8.1
/OPA4_IN-: C23.1, R16.2, R17.1, U8.2
/RS485_+5V: C56.1, C57.1, P3.4, U4.16
/RS485_A: P3.3, R8.1, U4.12
/RS485_B: P3.2, R8.2, U4.13
/RS485_D: IC1.1, U4.6
/RS485_DE: IC1.2, U4.5
/RS485_GND: C56.2, C57.2, P3.1, U4.9, U4.10, U4.15
/RS485_R: IC1.10, U4.3
/RS485_RE: IC1.9, U4.4
/SCLK: IC1.17, JP2.2, P5.3, R21.1, U3.3, U15.10, U17.10
/SCLK_ISO: JP2.1, U3.18, U13.11
/VLIM1: J1.1, R29.1, U5.3, W7.1
/VLIM2: J1.2, R26.1, U7.3, W10.1
/VLIM3: J3.1, R34.1, U6.3
/VLIM4: J3.2, R37.1, U8.3
Earth_Clean: C1.2, C2.2, C3.2, C4.2, C10.2, C11.2, C12.2, C13.2, C18.2, C19.2, C20.2, C21.2, C28.2, C29.2, C30.1, C31.2, C32.2, C43.2, C45.2, C46.2, C47.2, C48.2, C50.2, C52.2, C53.2, C54.2, C55.2, CON1.2, CON1.3, D1.2, D1.4, D5.1, D6.1, DB_GND1.1, DB_GND2.1, DB_GND3.1, DISABLE_OPA1.3, DISABLE_OPA2.3, DISABLE_OPA3.3, DISABLE_OPA4.3, IC1.3, IC1.5, IC1.21, J1.3, J3.3, P1.1, P1.2, P1.3, P1.4, P5.6, R3.2, R10.2, R11.1, R12.1, R14.1, R16.1, R18.1, R25.2, R28.2, R33.2, R36.2, R40.1, R41.1, R42.1, SW1.3, U1.2, U1.4, U2.2, U3.2, U3.10, U4.2, U4.7, U4.8, U5.4, U5.PAD, U6.4, U6.PAD, U7.4, U7.PAD, U8.4, U8.PAD, U11.9, U11.15, U14.4, U15.5, U15.6, U15.13, U15.14, U15.15, U15.16, U16.4, U17.5, U17.6, U17.13, U17.14, U17.15, U17.16, U18.2, U18.5, U18.7, U18.9, U18.12
unnamed: C4.1, JP1.3
unnamed: C30.2, IC1.7, X1.1
unnamed: C31.1, IC1.20
unnamed: C32.1, IC1.8, X1.2
unnamed: C39.1, U13.4
unnamed: C39.2, U13.5
unnamed: C41.1, U13.17
unnamed: C42.1, R24.1, R26.2, U14.1
unnamed: C42.2, R24.2, R25.1, U14.2
unnamed: C44.1, R27.1, R29.2, U14.7
unnamed: C44.2, R27.2, R28.1, U14.6
unnamed: C47.1, C48.1, U15.3
unnamed: C49.1, R32.1, R34.2, U16.1
unnamed: C49.2, R32.2, R33.1, U16.2
unnamed: C51.1, R35.1, R37.2, U16.7
unnamed: C51.2, R35.2, R36.1, U16.6
unnamed: C54.1, C55.1, U17.3
unnamed: C_filter1.1, R_gain1.1, U9.7
unnamed: C_filter2.1, R_gain2.1, U10.7
unnamed: D1.1, R1.2
unnamed: D1.3, R2.2
unnamed: D2.1, R3.1
unnamed: D3.1, U12.23
unnamed: D3.2, R22.1
unnamed: D4.1, U12.22
unnamed: D4.2, R23.1
unnamed: D5.2, R21.2
unnamed: D6.2, R43.1
unnamed: DISABLE_OPA1.2, U5.7
unnamed: DISABLE_OPA2.2, U7.7
unnamed: DISABLE_OPA3.2, U6.7
unnamed: DISABLE_OPA4.2, U8.7
unnamed: U11.3, U12.1
unnamed: U11.5, U12.5
VCC: C1.1, C10.1, C11.1, C12.1, C13.1, C18.1, C19.1, C20.1, C21.1, CON1.1, DB_VCC1.1, DB_VCC2.1, DB_VCC3.1, R9.1, U1.1, U5.5, U6.5, U7.5, U8.5

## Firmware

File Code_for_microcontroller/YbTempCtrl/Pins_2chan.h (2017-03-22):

/** @file
 *
 * Hardware limits and pins
 *
 * This file contains pin numbers and hard-coded limits specific to the 2
 * channel board
 *
 * OPA_GAIN is the gain of the OPA compared to the DAC's output voltage of 2.5V.
 * This is set by resistors on the board, calculated according to the values of
 * OPA_R1 and OPA_R2. It is currently assumed that both OPAs have the same gain.
 *
 * @todo Add option for user to configure different hardware gains on the two
 * OPAs.
 */

#pragma once

#include <Arduino.h>

// ADC pins
const uint8_t ADC_CS = A3; 					/*!< Chip select pin of the ADC on the ATMega */
const uint8_t ADC_START = 2;				/*!< ~START pin of the ADC on the ATMega */
const uint8_t ADC_DRDY = A2;				/*!< DRDY pin of the ADC on the ATMega */

// ADC channels
const uint8_t ADC_THERM1    = 9;    /*!< ADC channel for thermistor 1 input */
const bool    ADC_THERM1_HIGHRES    = false;    /*!< Should thermistor 1 be a high-res measurement? */
const uint8_t ADC_THERM2		= 8;		/*!< ADC channel for thermistor 2 input */
const bool    ADC_THERM2_HIGHRES    = false;    /*!< Should thermistor 2 be a high-res measurement? */
const uint8_t ADC_REF			= 10;		/*!< ADC channel for common thermistor reference input */
const uint8_t ADC_VOLT1_P		= 6;		/*!< ADC channel for arbitary voltage positive input 1 */
const uint8_t ADC_VOLT1_N		= 7;		/*!< ADC channel for arbitary voltage negative input 1 */
const bool    ADC_VOLT1_HIGHRES    = false;    /*!< Should voltage 1 be a high-res measurement? */
const uint8_t ADC_VOLT2_P		= 4;		/*!< ADC channel for arbitary voltage positive input 2 */
const uint8_t ADC_VOLT2_N		= 5;		/*!< ADC channel for arbitary voltage negative input 2 */
const bool    ADC_VOLT2_HIGHRES    = false;    /*!< Should voltage 2 be a high-res measurement? */
const uint8_t ADC_TMP			= 11;		/*!< ADC channel for chip temperature measurement */
const uint8_t ADC_POW			= 12;		/*!< ADC channel for chip power level measurement */

// DAC pins
const uint8_t DAC_CS 			= 9;		/*!< Chip select pin of the DAC on the ATMega */
const uint8_t OPA_ES1 			= A0;		/*!< E/S pin for first OPA */
const uint8_t OPA_ES2 			= A1;		/*!< E/S pin for second OPA */
const bool OPA_1_IS_548			= false;	/*!< Is OPA 1 an OPA548 (instead of an OPA549)? */
const bool OPA_2_IS_548			= false;	/*!< Is OPA 2 an OPA548 (instead of an OPA549)? */

// DAC channels
const uint8_t VPLUS_CHAN_1 	= 1;			/*!< DAC channel for first OPA's V+ input */
const uint8_t VPLUS_CHAN_2 	= 0;			/*!< DAC channel for second OPA's V+ input */
const uint8_t VLIM_CHAN_1 	= 3;			/*!< DAC channel for first OPA's Vlim input */
const uint8_t VLIM_CHAN_2 	= 2;			/*!< DAC channel for second OPA's Vlim input */

// OPA settings
extern double MAX_VOLTAGE;					/*!< Maximum voltage for the OPAs to output. Calculated in setup() */
const double MAX_INITIAL_CURRENT = 2.0;		/*!< Maximum current that the OPAs will be limited to on startup */
const double OPA_R1	= 40.2;					/*!< OPA gain resistor 1 */
const double OPA_R2	= 200.2;					/*!< OPA gain resistor 2 */
const double OPA_GAIN = 
			(OPA_R1 + OPA_R2) / OPA_R1;		/*!< DAC -> OPA gain, set by on-board resistors. */

// LED output pins
const uint8_t LED_1 = A5; 					/*!< ATMega pin for LED 1, Arduino labelling */
const uint8_t LED_2 = A4;					/*!< ATMega pin for LED 2, Arduino labelling */

// Other Microprocessor pins
const uint8_t DISABLE_SERIAL_CTRL = 0xFF; 	/*!< ATMega pin for disabling serial control: 0 or 5V (set to 0xFF if not present) */
const uint8_t DIVIDED_SUPPLY_VOLTAGE = 0xFF;/*!< ATMega pin for reading supply voltage: analog voltage (set to 0xFF if not present) */
const double FALLBACK_SUPPLY_VOLTAGE = 15;	/*!< Assumed supply voltage if DIVIDED_SUPPLY_VOLTAGE pin is not present */
const double DIVIDED_SUPPLY_FACTOR = 0;		/*!< Factor by which the supply voltage has been divided  */

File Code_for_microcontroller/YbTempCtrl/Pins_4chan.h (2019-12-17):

/** @file
 *
 * Hardware limits and pins
 *
 * This file contains pin numbers and hard-coded limits specific to the 4
 * channel board
 *
 * OPA_GAIN is the gain of the OPA compared to the DAC's output voltage of 2.5V.
 * This is set by resistors on the board, calculated according to the values of
 * OPA_R1 and OPA_R2. It is currently assumed that both OPAs have the same gain.
 *
 * @todo Add option for user to configure different hardware gains on the two
 * OPAs.
 */

#pragma once

#include <Arduino.h>

#define FOUR_CHANNEL_BOARD

#define VERSION_5
// #define VERSION_4

// ADC pins
const uint8_t ADC_CS = A3; 					/*!< Chip select pin of the ADC on the ATMega */
const uint8_t ADC_START = 2;				/*!< ~START pin of the ADC on the ATMega */
const uint8_t ADC_DRDY = A2;				/*!< DRDY pin of the ADC on the ATMega */

// ADC channels
const uint8_t ADC_THERM1    = 9;    /*!< ADC channel for thermistor 1 input */
const bool    ADC_THERM1_HIGHRES    = false;    /*!< Should thermistor 1 be a high-res measurement? */
const uint8_t ADC_THERM2    = 8;    /*!< ADC channel for thermistor 2 input */
const bool    ADC_THERM2_HIGHRES    = false;    /*!< Should thermistor 2 be a high-res measurement? */
const uint8_t ADC_REF     = 10;   /*!< ADC channel for common thermistor reference input */
const uint8_t ADC_TMP     = 11;   /*!< ADC channel for chip temperature measurement */
const uint8_t ADC_POW     = 12;   /*!< ADC channel for chip power level measurement */

const uint8_t ADC_TESTER = 7;

// DAC pins
const uint8_t DAC_CS 			= 10;		/*!< Chip select pin of the DAC on the ATMega */
const bool OPA_1_IS_548			= true;		/*!< Is OPA 1 an OPA548 (instead of an OPA549)? */
const bool OPA_2_IS_548			= true;		/*!< Is OPA 2 an OPA548 (instead of an OPA549)? */

// 2nd DAC pins
const uint8_t DAC_CS_Alt 		= 9;		/*!< Chip select pin of the DAC on the ATMega */
const bool OPA_3_IS_548			= true;		/*!< Is OPA 1 an OPA548 (instead of an OPA549)? */
const bool OPA_4_IS_548			= true;		/*!< Is OPA 2 an OPA548 (instead of an OPA549)? */

// E/S pins
#ifdef VERSION_5
	const bool ES_FLOAT_ON = false;    /*!< Should the E/S pins float or be driven high to enable the OPAs? */
	const uint8_t OPA_ES1 			= 8;		/*!< E/S pin for first OPA */
	const uint8_t OPA_ES2 			= 7;		/*!< E/S pin for second OPA */
	const uint8_t OPA_ES3 			= A0;		/*!< E/S pin for first OPA */
	const uint8_t OPA_ES4 			= A1;		/*!< E/S pin for second OPA */
#endif
#ifdef VERSION_4
	const bool ES_FLOAT_ON = true;    /*!< Should the E/S pins float or be driven high to enable the OPAs? */
	const uint8_t OPA_ES1 			= A1;		/*!< E/S pin for first OPA */
	const uint8_t OPA_ES2 			= A0;		/*!< E/S pin for second OPA */
	const uint8_t OPA_ES3 			= 8;		/*!< E/S pin for first OPA */
	const uint8_t OPA_ES4 			= 7;		/*!< E/S pin for second OPA */
#endif

// DAC channels
const uint8_t VPLUS_CHAN_1 	= 0;			/*!< DAC channel for second OPA's V+ input */
const uint8_t VPLUS_CHAN_2 	= 1;			/*!< DAC channel for first OPA's V+ input */
const uint8_t VLIM_CHAN_1 	= 3;			/*!< DAC channel for second OPA's Vlim input */
const uint8_t VLIM_CHAN_2 	= 2;			/*!< DAC channel for first OPA's Vlim input */

// 2nd DAC channels
const uint8_t VPLUS_CHAN_3 	= 0;			/*!< DAC channel for second OPA's V+ input */
const uint8_t VPLUS_CHAN_4 	= 1;			/*!< DAC channel for first OPA's V+ input */
const uint8_t VLIM_CHAN_3 	= 2;			/*!< DAC channel for second OPA's Vlim input */
const uint8_t VLIM_CHAN_4 	= 3;			/*!< DAC channel for first OPA's Vlim input */

// OPA settings
extern double MAX_VOLTAGE;					/*!< Maximum voltage for the OPAs to output. Calculated in setup() */
const double MAX_INITIAL_CURRENT = 2.0;		/*!< Maximum current that the OPAs will be limited to on startup */
const double OPA_R1	= 50;					/*!< OPA gain resistor 1 */
const double OPA_R2	= 200;					/*!< OPA gain resistor 2 */
const double OPA_GAIN = 
			(OPA_R1 + OPA_R2) / OPA_R1;		/*!< DAC -> OPA gain, set by on-board resistors. */

// LED output pins
const uint8_t LED_1 = A5; 					/*!< ATMega pin for LED 1, Arduino labelling */
const uint8_t LED_2 = A4;					/*!< ATMega pin for LED 2, Arduino labelling */

// Other Microprocessor pins
const uint8_t DISABLE_SERIAL_CTRL = A6; 	/*!< ATMega pin for disabling serial control: 0 or 5V */
const uint8_t DIVIDED_SUPPLY_VOLTAGE = A7; 	/*!< ATMega pin for reading supply voltage: analog voltage */
const double DIVIDED_SUPPLY_FACTOR = 11.0;	/*!< Factor by which the supply voltage has been divided  */
const double FALLBACK_SUPPLY_VOLTAGE = 15;	/*!< Assumed supply voltage if DIVIDED_SUPPLY_VOLTAGE pin is not present */

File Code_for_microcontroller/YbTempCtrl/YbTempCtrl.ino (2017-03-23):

/*-------------------------------------------------------------------
-																	-
-		PID Temperature Controller									-
-			Charles Baynham - NPL									-
-																	-
-		Version:													-
-*/
#define REV_VERSION "v4.3"									
#define IDENTIFIER "ARDUINO PID"
/*																	-
-		Controller to manage up to two processes, correcting them	-
-		via a PID algorithm.										-
-																	-
-		By default, this controller communicates by USB-serial		-
-		connection. The Serial connection expects:					-
-			Baud rate: 56700										-
-			Data: 8 bits, Parity: NO, Stop bits: 1					-
-		Comms must be terminated by the '\n' char.					-
-																	-
--------------------------------------------------------------------*/

#pragma message ("Implement *TST")

#include "Pins.h"

// Num of s.f. to print floats with
#define FLT_PRINT_PRECISION 9

// Library to measure free memory
#include "MemoryFree.h"

// Library to parse and handle commands, and store startup commands in EEPROM
#include "CommandHandler\CommandHandler.h"

// Library to toggle pins at a defined rate
#include "arduino-pin-toggler\pinToggler.h"

// Objects specific to this code:
#include "Controller.h"
#include "PIDAlgorithm.h"
#include "V4_ADC_ChannelPair.h"
#include "V4_OPA_OutputChannel.h"
#include "V4_OPA_OutputChannelBipolar.h"

using namespace YbCtrl;

// Not used here, but these are needed by class files so must be included here
#include <SPI.h>

// Macros for the watchdog timer
#include <avr/wdt.h>

// Header containing the latest GIT hash
#include "latest_hash.h"

// Convenience macros for debugging
#include "Microprocessor_debugging\debugging_init.h"
#include "Microprocessor_debugging\debugging_disable.h"

// Command handler object, can hold 30 commands
CommandHandler<32> handler;
// Declare functions for all the SCPI commands
#include "CommandDefinitions.h"

// Default thresholds for the LED flash rate indicators (in volts)
double led_thresholds[2] = { 0.1, 0.01 };

// Max voltage that the OPA will attempt to output
// This is calculated by measuring the supply voltage (using a divided voltage on pin DIVIDED_SUPPLY_VOLTAGE)
// and subtracting 0.3V since the OPAs are not rail-to-rail
double MAX_VOLTAGE = 0;						

// Vector for pointers to the input channels
#ifdef FOUR_CHANNEL_BOARD
	ErrorChannel * errorChannels[5];
#else
	ErrorChannel * errorChannels[7];
#endif

// Labels for each of the error channels
#ifdef FOUR_CHANNEL_BOARD
enum class ErrorChanIdx {
	NOT_FOUND = -1,
	CHAN_1T, // == 0
	CHAN_2T, // == 1
	CHAN_TMP, // etc
	CHAN_POW
};
#else
enum class ErrorChanIdx {
	NOT_FOUND = -1,
	CHAN_1T, // == 0
	CHAN_2T, // == 1
	CHAN_1V, // etc.
	CHAN_2V,
	CHAN_TMP,
	CHAN_POW
};
#endif

// Vector for pointers to the output channels
// These are (carefully) malloced in setup()
#ifdef FOUR_CHANNEL_BOARD
CtrlChannel * ctrlChannels[6];
#else
CtrlChannel * ctrlChannels[3];
#endif

// Labels for each of the output channels
#ifdef FOUR_CHANNEL_BOARD
enum class CtrlChanIdx {
	NOT_FOUND = -1,
	CHAN_1,
	CHAN_2,
	CHAN_3,
	CHAN_4,
	CHAN_BP_12,
	CHAN_BP_34
};
#else
enum class CtrlChanIdx {
	NOT_FOUND = -1,
	CHAN_1,
	CHAN_2,
	CHAN_BP_12
};
#endif

// DFU mode magic variable
// This variable is not initialised to zero. Therefore we can write to it before a watchdog 
// reset and it won't get overridden, so we can send information from instance to instance. 
// I'll use this to send a "magic key" which, if it is set, means that I'm requesting a bootloader reset
const uint16_t magic_bootloader_key = 0x586c;
uint16_t boot_key __attribute__ ((section (".noinit")));
unsigned int num_resets __attribute__ ((section (".noinit")));

// Reserve space for things
//
// 1) Controllers (not pointers, this reserves space on the stack)
//
// This vector will be 2 long, containing Controllers or nullptrs.
//
// This is the most we can need at one time: we can control channel 1 and
// channel 2 independently (2 Controllers), or both simultaneously in a bipolar
// configuration (1 Controller).
//
// The program will assign Controllers onto this buffer in the order that they are created
// (i.e. when the user calls ("LOCK")
//
// 2) PIDAlgorithms
// 
// Algorithms are stored with the same index as their associated Controller
#ifdef FOUR_CHANNEL_BOARD
Controller controllers[4];
PIDAlgorithm pidAlgorithms[4];
#else
Controller controllers[2];
PIDAlgorithm pidAlgorithms[2];
#endif

// The Arduino IDE will automatically define all the functions declared in this file, but it will fail on those that require a namespace
// Since all the YbTempCtrl related objects use the YbCtrl namespace, all functions that take a parameter relating to one of these objects
// must be declared manually. 
// They are all declared "static" using the C meaning of the modifier: i.e. these functions only exist within this file
static void closeChannelsController(CtrlChannel * chan);
static void reportCtrlError(CtrlChannelReturn err);
static void reportErrorError(ErrorChannelReturn err);
static inline bool voltageToBeDoubled(const ErrorChanIdx chan);
static ErrorChanIdx stringToADCChannel(const char str[]);
static CtrlChanIdx stringToOPAChannel(const char str[]);
static inline bool isBipolar(const CtrlChanIdx chan);

const size_t numLEDs = 2;

// If this variable is true, serial control will be enabled regardless of the switch position
bool _forceSerialEnabled = true;
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

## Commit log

2017-01-11 Start combined repo
    This repo contains all the parts of the temperature controller.
    All submodules have been removed and replaced with raw files.
    [ADC_Buffers.sch, ADC_Chip.sch, BOM.xlsx, BPSubsheet.sch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]
2017-01-12 Label microfit connector
2017-01-19 Add CAD model of rack unit
    [20817443.SLDASM, 20817443_01.SLDPRT, 20817443_02.SLDPRT, 20817443_03.SLDPRT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]
2017-02-02 Front panel alterations
    [20817443.SLDASM, Drawing.SLDDRW, Panel drawing.SLDDRW, Panel-recognised.SLDPRT]
2017-02-22 Front panel annotations
    [Panel drawing.SLDDRW]
2017-03-08 Make LEDs deterministically assigned
    Also:
    Update manual to reflect LED changes
    Squashed commit:
    [38ef2a3] Ignore intermediate Tex files
2017-03-21 Rename BP to BPA in the 2 channel board
2017-03-21 Pins for the 2 channel board
2017-03-22 Correct resistance for 934 temperature controller
2018-09-10 Update to fix latex KiCad breakages
    [ADC_Chip.sch, DACOutputs.sch, DIYino.sch, INA330.sch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]
2019-04-17 Update to Kicad v5.0 (almost)
    [ADC_Chip-2019-04-17-16-30-30.sch, DACOutputs-2019-04-17-16-30-30.sch, DIYino-2019-04-17-16-30-30.sch, INA330-2019-04-17-16-30-30.sch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]
2019-04-17 Correct schematic (with help of Kicad v5.1)
    [ADC_Chip.sch, DACOutputs.sch, DIYino.sch, INA330.sch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]
2019-04-17 Update PCB, removing some but not all of the courtyard failures
    [TempCtrl.kicad_pcb]
2019-04-17 Add more testpoints and change to the single hoop style
    [TempCtrl.kicad_pcb, TempCtrl.sch]
2019-04-23 Add buffers to E/S pins on schematic
    [ADC_Chip.sch, DACOutputs.sch, DIYino.sch, ES_Buffers.sch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]
2019-04-23 Start PCB
    [DACOutputs.sch, DIYino.sch, ES_Buffers.sch, INA330.sch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]
2019-04-23 Add to board
    [TempCtrl.kicad_pcb, TempCtrl.sch]
2019-04-23 Change to newer resistors with smaller courtyards
    [TempCtrl.kicad_pcb, TempCtrl.sch]
2019-04-23 Add to PCB
    [TempCtrl.kicad_pcb]
2019-10-15 Schematic changes for v5
    [ADC_Chip.sch, DACOutputs.sch, DIYino.sch, ES_Buffers.sch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]
2019-10-16 Update schematic with v5 changes
    [ADC_Chip.sch, DACOutputs.sch, DIYino.sch, ES_Buffers.sch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]
2019-10-16 Schematic: daughter board and MMCX ref
    [ADC_Chip.sch, DACOutputs.sch, DIYino.sch, ES_Buffers.sch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]
2019-10-16 Pass PCB DRC with new footprint courtyards
    [TempCtrl.kicad_pcb, TempCtrl.sch]
2019-10-16 PCB: buffer, ext ref, OPA jumpers, MMCX conn
    [TempCtrl.kicad_pcb, TempCtrl.sch]
2019-10-16 Replace VCC routes with fill on internal layer, where 5V isn't needed
    [TempCtrl.kicad_pcb]
2019-10-16 PCB: Connections for daughterboard
    [DACOutputs.sch, TempCtrl.kicad_pcb, TempCtrl.sch]
2019-10-16 PCB: Mount points
    [TempCtrl.kicad_pcb]
2019-10-16 BOTH: Add 5V daughterboard point
    [DACOutputs.sch, TempCtrl.kicad_pcb, TempCtrl.sch]
2019-10-16 Comments and mount positions
    [INA330.sch, TempCtrl.kicad_pcb, TempCtrl.sch]
2019-10-16 Store all non-generic parts in schematic
    [ADC_Chip.sch, BOM.xlsx, DACOutputs.sch, DIYino.sch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]
2019-10-16 Complete BOM
    [BOM.xlsx, TempCtrl.sch]
2019-10-16 Compile for V5 assembly
    [TempCtrl-B_Cu.gbl, TempCtrl-B_Mask.gbs, TempCtrl-B_Paste.gbp, TempCtrl-B_SilkS.gbo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]
2019-10-24 Correct barrel jack part number, update pdf schematic
    [ADC_Chip.sch, BOM.xlsx, DACOutputs.sch, DIYino.sch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]
2019-11-14 Organise front panel files and fix error in BOM
    [20817443.SLDASM, 20817443_01.SLDPRT, 20817443_02.SLDPRT, 20817443_03.SLDPRT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]
2019-11-18 Fix more BOM mistakes
    [BOM.xlsx, ES_Buffers.sch]
2019-12-04 Correct MFN of buffer chip, and use new BOM generator
    [BOMAlt.xlsx, ES_Buffers.sch]
2019-12-11 Label JP1
    [TempCtrl.kicad_pcb]
2019-12-17 Move trace on rear to avoid heatsink pad
    [TempCtrl.kicad_pcb]
2019-12-17 Alter E/S pin behaviour for new buffer chip
2020-02-25 Bump version and output
    [TempCtrl-B_Cu.gbl, TempCtrl-B_Mask.gbs, TempCtrl-B_Paste.gbp, TempCtrl-B_SilkS.gbo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]
2020-02-25 Add BOM to Zip file
    [BOM.xlsx, BOMAlt.xlsx]
2020-03-24 Move resistor to not foul ICSP connector in BOM
    [TempCtrl-B_Cu.gbl, TempCtrl-B_Mask.gbs, TempCtrl-B_Paste.gbp, TempCtrl-B_SilkS.gbo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]
2020-04-08 Reduce size of paste for OPA548s
    [TempCtrl-B_Cu.gbl, TempCtrl-B_Mask.gbs, TempCtrl-B_Paste.gbp, TempCtrl-B_SilkS.gbo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]
2021-01-26 Expand courtyard of connector
    [TempCtrl.kicad_pcb]
2021-01-26 Version bump and compile
    [ADC_Chip-2019-04-17-16-30-30.sch, DACOutputs-2019-04-17-16-30-30.sch, DIYino-2019-04-17-16-30-30.sch, INA330-2019-04-17-16-30-30.sch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]
2021-01-27 Remove extra sheet from BOM
    [BOM.xlsx]
2021-01-29 Enlarge LED holes
    [Temperature controller V5 - 3U4HP.SLDPRT]
2021-04-09 Add drawings
    [Quotation from Elecrow.xlsx, Temperature controller V5 - 3U4HP.SLDDRW]
2021-04-09 Move resistors slightly to avoid ISCP connector
    [TempCtrl-B_Cu.gbl, TempCtrl-B_Mask.gbs, TempCtrl-B_Paste.gbp, TempCtrl-B_SilkS.gbo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]
2021-04-12 Move isolator too: that connector is massive
    [TempCtrl-B_Cu.gbl, TempCtrl-B_Mask.gbs, TempCtrl-B_Paste.gbp, TempCtrl-B_SilkS.gbo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]
2021-04-13 Remove VLIM capacitors - these were pushing opamps dangerously close to instability
    [DACOutputs.sch, TempCtrl.kicad_pcb, TempCtrl.sch]
2021-04-13 Update BOM and gerbers
    [BOM.xlsx, TempCtrl-B_Cu.gbl, TempCtrl-B_Mask.gbs, TempCtrl-B_Paste.gbp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]
2021-04-13 Fix schematic for ATMega (no changes to board)
    [DACOutputs.sch, DIYino.sch]
2021-04-21 Expand footprint of U18
    [ADC_Chip.sch, DACOutputs.sch, DIYino.sch, ES_Buffers.sch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]
